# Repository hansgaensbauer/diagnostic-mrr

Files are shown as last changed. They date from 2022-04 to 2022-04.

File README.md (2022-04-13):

# Low Cost MRR For Malaria Diagnosis

This project is a low-cost, low complexity version of the instrument presented by Peng, Chen, and Han in [Development of miniaturized, portable magnetic resonance relaxometry system for point-of-care medical diagnosis](https://aip.scitation.org/doi/citedby/10.1063/1.4754296), used by Peng et al. in [Micromagnetic resonance relaxometry for rapid label-free malaria diagnosis](https://www.nature.com/articles/nm.3622). 

This tool attempts to significantly lower the cost of an instrument capable of diagnosing malaria and other diseases by stripping the researchers' design of all functionality that is not absolutely necessary for this specific application. Notably, this is done by:
1. Modifying the magnet holder so that the separation between the magnets on either side of the sample can be adjusted. This allows the larmor frequency for proton MRR to be tuned to an easily obtaiable frequency. 
2. Generating the CPMG pulse train and the 20MHz carrier with a cheap microcontroller (ATMEGA328P)
3. Replacing COTS RF components with custom implementations using cheap passives and transistors wherever possible
4. Implementing the receiver with tuned filters and peak detect circuits

## New Hardware
These PCBs have been ordered, manufactured, and shipped. They will make testing and calibration much more controlled and repeatable. 
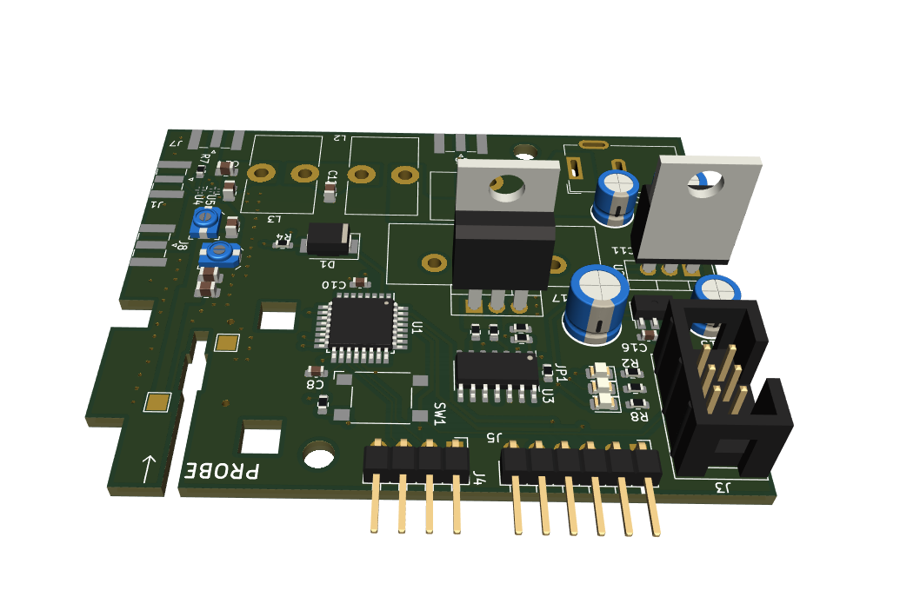
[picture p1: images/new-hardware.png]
New PCB


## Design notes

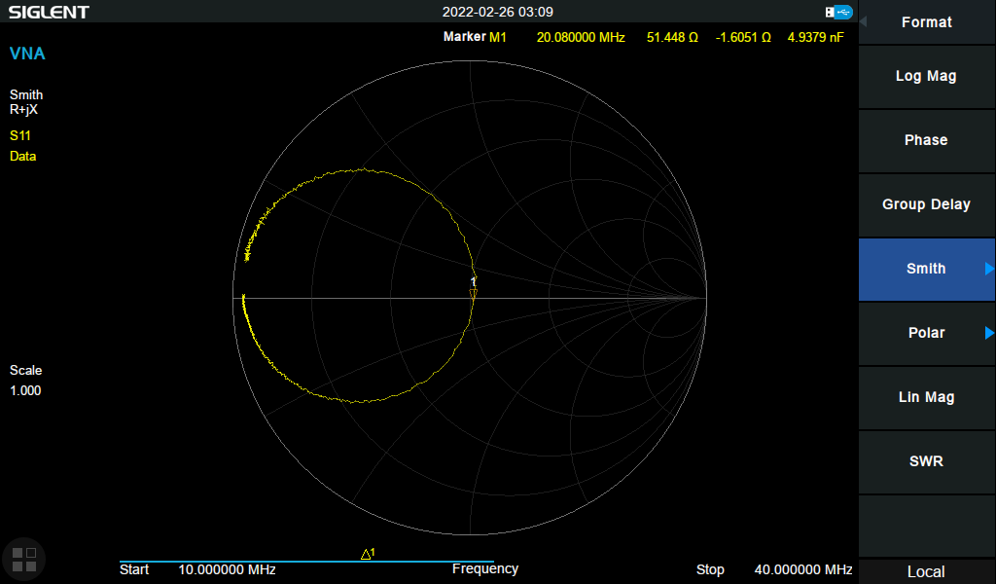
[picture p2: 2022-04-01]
images/Probe-Smith.png

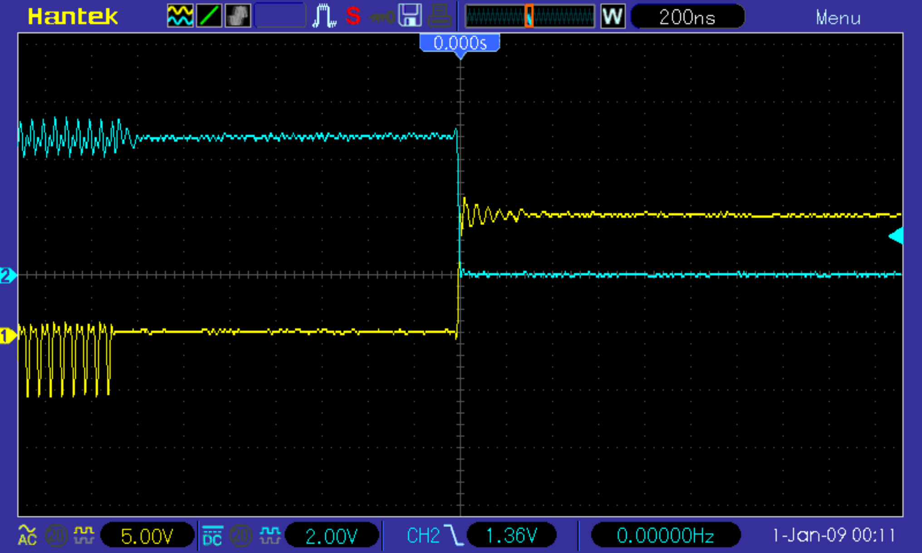
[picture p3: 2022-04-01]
images/dead-time.png

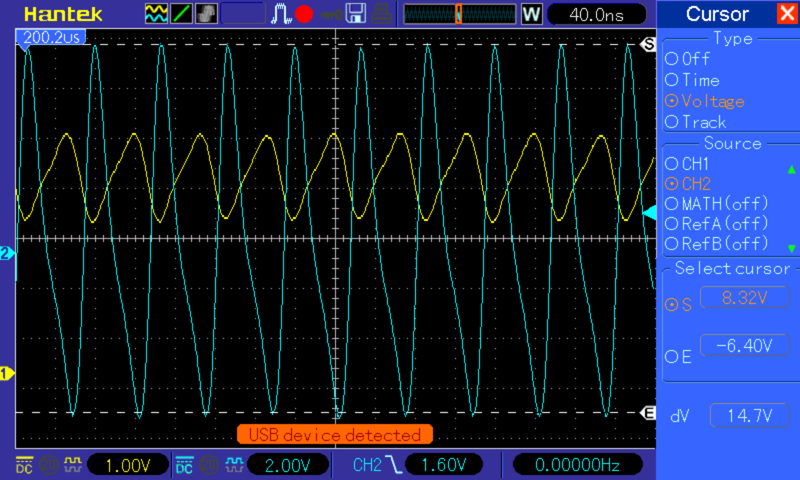
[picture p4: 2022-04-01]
images/pa-1w.png

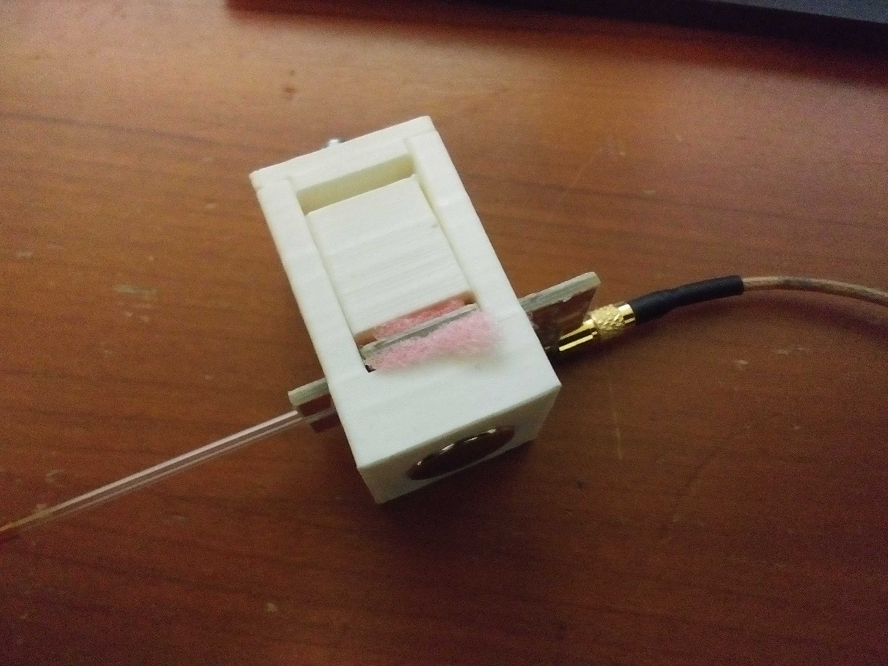
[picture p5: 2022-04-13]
images/Probe-V1.jpg

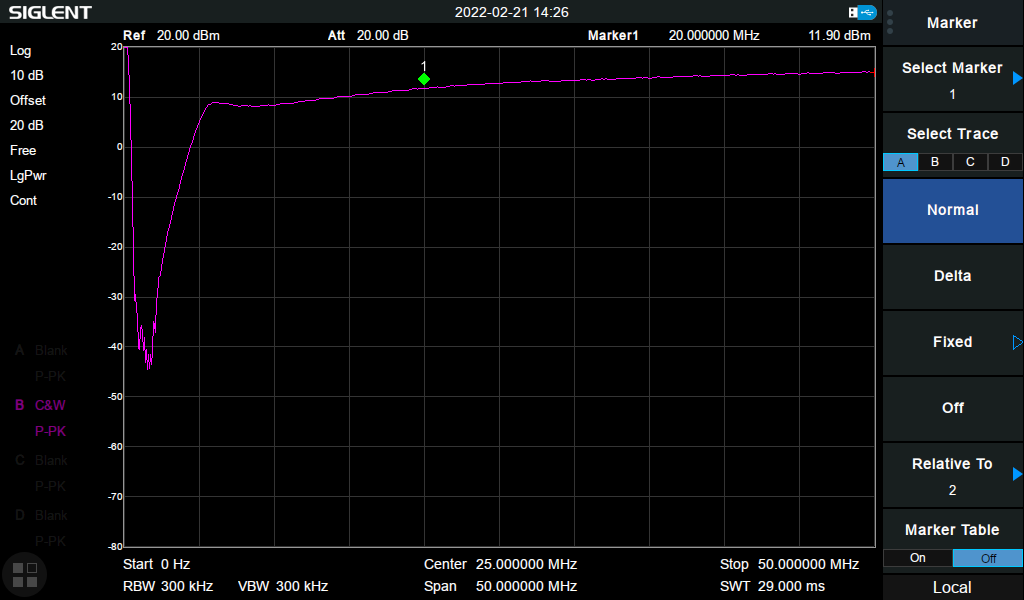
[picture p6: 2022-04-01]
images/rtl-sdr-lna.png

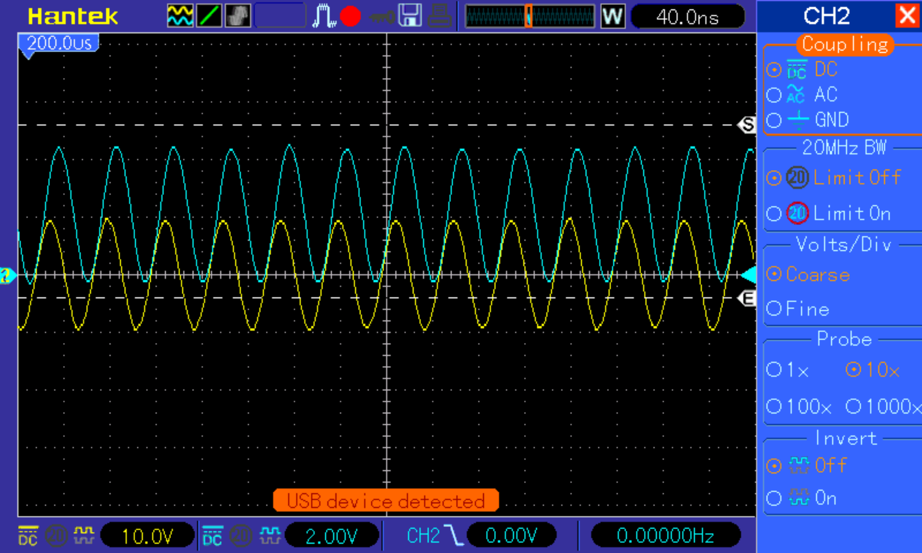
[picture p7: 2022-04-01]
images/pa-firstpass.png

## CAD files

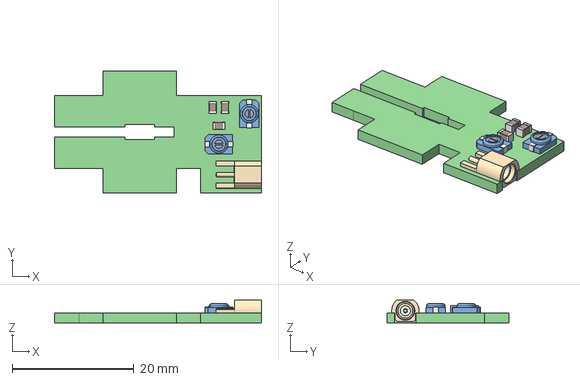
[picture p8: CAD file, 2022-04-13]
Hardware/probe/probe.step
34.0 x 20.0 x 3.75 mm
probe PCB

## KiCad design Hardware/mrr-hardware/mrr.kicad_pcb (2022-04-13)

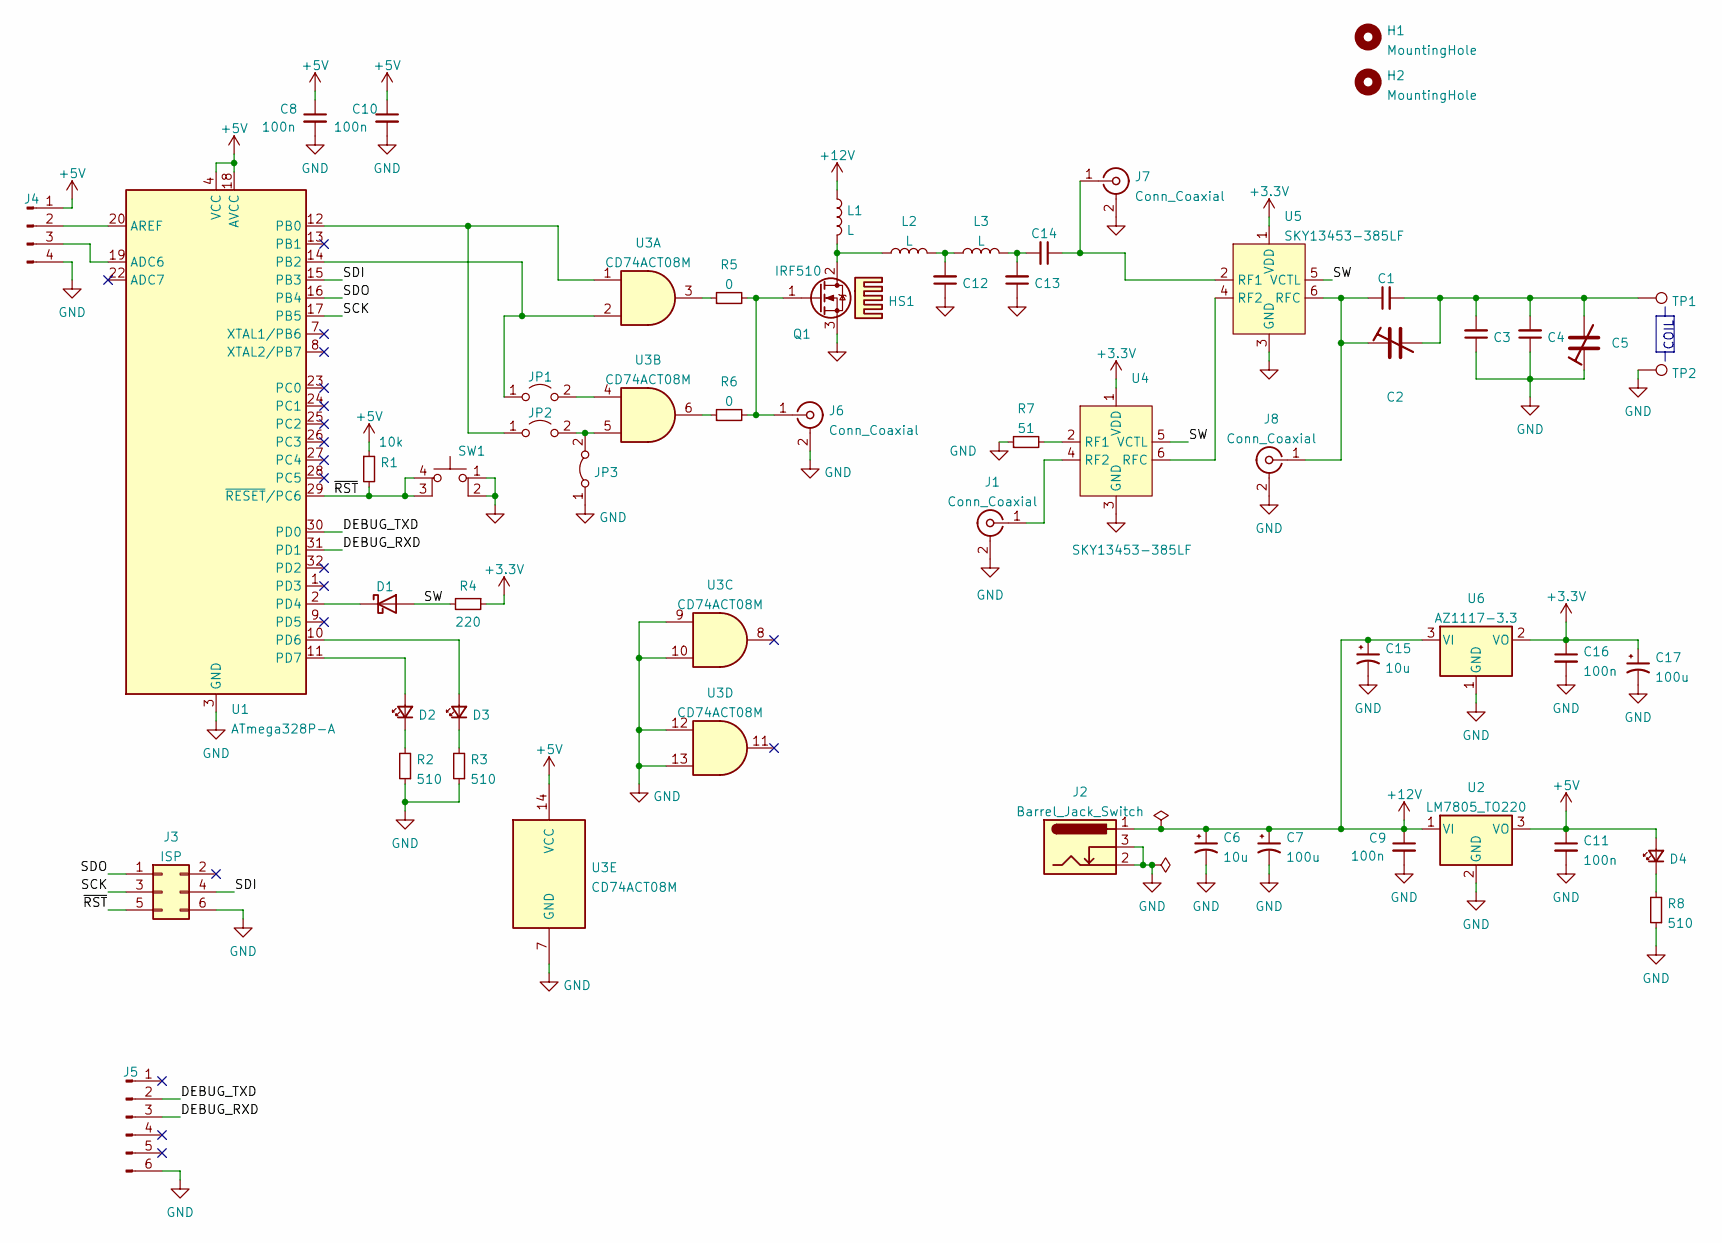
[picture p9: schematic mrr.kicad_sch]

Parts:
C1, C3, C4, C12, C13, C14: C_Small; C_0805_2012Metric
C2, C5: C_Trim; C_Trimmer_Sprague-Goodman_SGC3
C6, C15: 10u; CP_Radial_D5.0mm_P2.00mm
C7, C17: 100u; CP_Radial_D6.3mm_P2.50mm
C8, C9, C10, C11, C16: 100n; C_0603_1608Metric
D1: D_Schottky; D_SMB
D2, D3, D4: LED_Small; LED_0805_2012Metric
H1, H2: MountingHole; MountingHole_3.2mm_M3
HS1: Heatsink; BIG_HEATSINK
J1, J6, J7, J8: Conn_Coaxial; SMA_Samtec_SMA-J-P-X-ST-EM1_EdgeMount
J2: Barrel_Jack_Switch; BarrelJack_Wuerth_6941xx301002
J3: ISP; IDC-Header_2x03_P2.54mm_Vertical
J4: Conn_01x04_Male; PinHeader_1x04_P2.54mm_Horizontal
J5: Conn_01x06_Male; PinHeader_1x06_P2.54mm_Horizontal
JP1, JP2: Jumper_2_Open; R_0603_1608Metric
JP3: Jumper_2_Bridged; R_0603_1608Metric
L1, L2, L3: L; L_Toroid_Vertical_L14.7mm_W8.6mm_P5.58mm_Pulse_KM-1
Q1: IRF510; TO-220-3_Vertical
R1: 10k; R_0603_1608Metric
R2, R3, R8: 510; R_0603_1608Metric
R4: 220; R_0603_1608Metric
R5, R6: 0; R_0603_1608Metric
R7: 51; R_0603_1608Metric
SW1: SW_MEC_5E; SW_SPST_Omron_B3FS-100xP
TP1, TP2: TestPoint; TestPoint_Pad_2.0x2.0mm
U1: ATmega328P-A; TQFP-32_7x7mm_P0.8mm
U2: LM7805_TO220; TO-220-3_Vertical
U3: CD74ACT08M; SOIC-14_3.9x8.7mm_P1.27mm
U4, U5: SKY13453-385LF; 6-XFQFN
U6: AZ1117-3.3; SOT-89-3

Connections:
+3V3: C16.1, C17.1, R4.1, U4.1 (VDD), U5.1 (VDD), U6.2 (VO)
+5V: C8.1, C10.1, C11.1, D4.2 (A), J4.1, R1.1, U1.4 (VCC), U1.6 (VCC), U1.18 (AVCC), U2.3 (VO), U3.14 (VCC)
+12V: C6.1, C7.1, C9.1, C15.1, J2.1, L1.1, U2.1 (VI), U6.3 (VI)
/DEBUG_RXD: J5.3, U1.31 (PD1)
/DEBUG_TXD: J5.2, U1.30 (PD0)
/SCK: J3.3, U1.17 (PB5)
/SDI: J3.4, U1.15 (PB3)
/SDO: J3.1, U1.16 (PB4)
/SW: D1.2 (A), R4.2, U4.5 (VCTL), U5.5 (VCTL)
/~RST: J3.5, R1.2, SW1.3 (K), SW1.4 (A), U1.29 (~RESET/PC6)
GND: C3.1, C4.1, C5.1, C6.2, C7.2, C8.2, C9.2, C10.2, C11.2, C12.1, C13.1, C15.2, C16.2, C17.2, J1.2 (Ext), J2.2, J2.3, J3.6, J4.4, J5.6, J6.2 (Ext), J7.2 (Ext), J8.2 (Ext), JP3.1 (A), Q1.3 (S), R2.1, R3.1, R7.1, R8.1, SW1.1, SW1.2, TP2.1, U1.3 (GND), U1.5 (GND), U1.21 (GND), U2.2 (GND), U3.7 (GND), U3.9, U3.10, U3.12, U3.13, U4.3 (GND), U5.3 (GND), U6.1 (GND)
unnamed: C1.1, C2.1, J8.1 (In), U5.6 (RFC)
unnamed: C1.2, C2.2, C3.2, C4.2, C5.2, TP1.1
unnamed: C12.2, L2.2, L3.1
unnamed: C13.2, C14.2, L3.2
unnamed: C14.1, J7.1 (In), U5.2 (RF1)
unnamed: D1.1 (K), U1.2 (PD4)
unnamed: D2.1 (K), R2.2
unnamed: D2.2 (A), U1.11 (PD7)
unnamed: D3.1 (K), R3.2
unnamed: D3.2 (A), U1.10 (PD6)
unnamed: D4.1 (K), R8.2
unnamed: J1.1 (In), U4.4 (RF2)
unnamed: J4.2, U1.20 (AREF)
unnamed: J4.3, U1.19 (ADC6)
unnamed: J6.1 (In), Q1.1 (G), R5.2, R6.2
unnamed: JP1.1 (A), U1.14 (PB2), U3.2
unnamed: JP1.2 (B), U3.4
unnamed: JP2.1 (A), U1.12 (PB0), U3.1
unnamed: JP2.2 (B), JP3.2 (B), U3.5
unnamed: L1.2, L2.1, Q1.2 (D)
unnamed: R5.1, U3.3
unnamed: R6.1, U3.6
unnamed: R7.2, U4.2 (RF1)
unnamed: U4.6 (RFC), U5.4 (RF2)

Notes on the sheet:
COIL

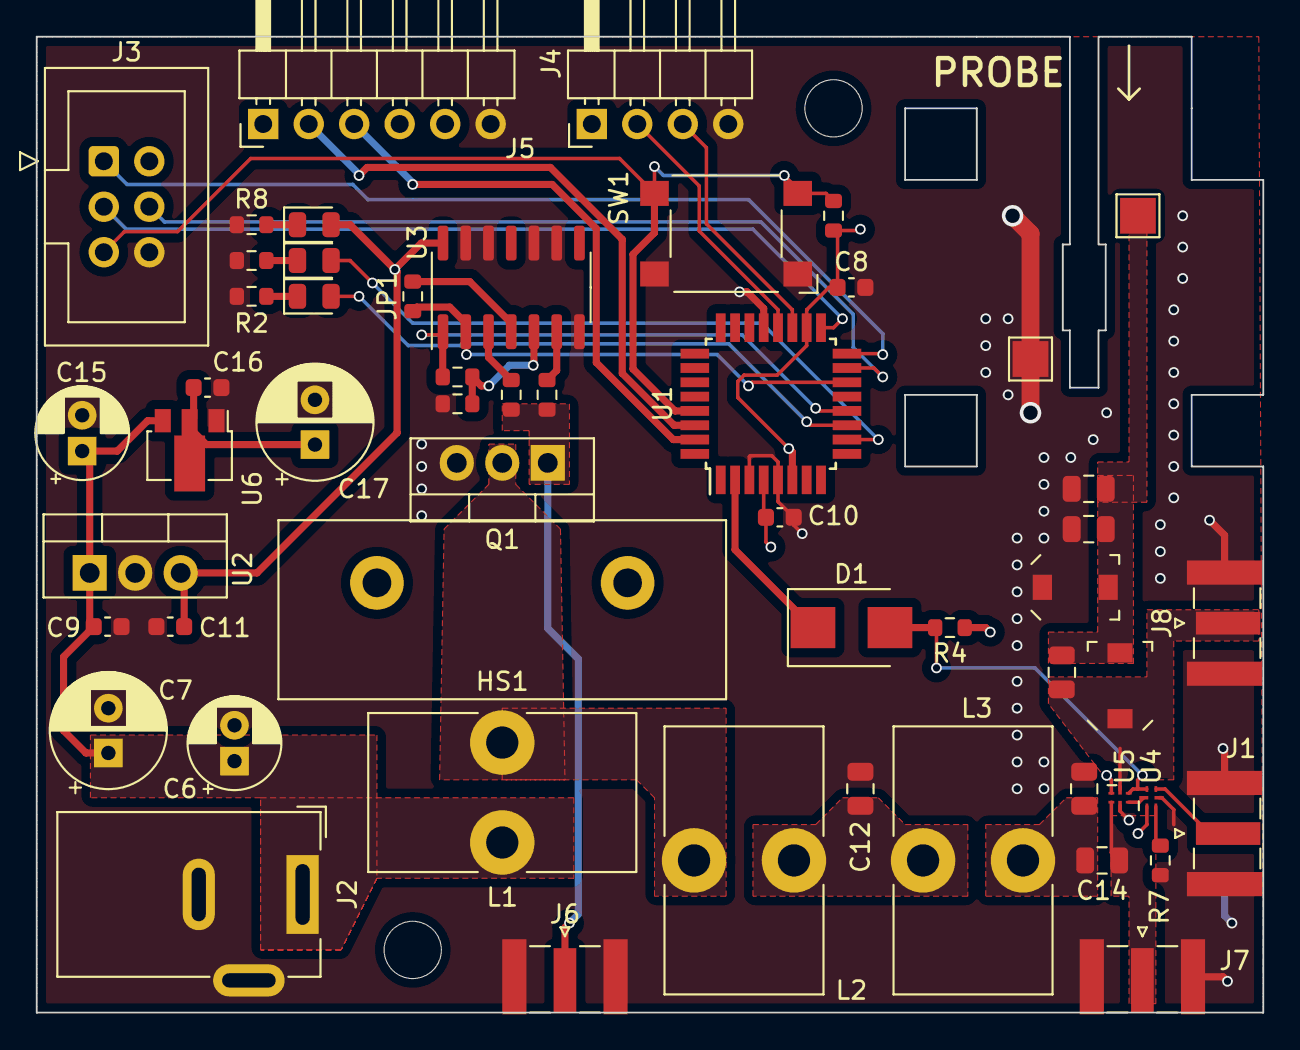
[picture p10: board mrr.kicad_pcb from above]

Board: 4 copper layers, 68.5 x 54.5 mm, 56 parts (0 on the bottom side), 35 nets.

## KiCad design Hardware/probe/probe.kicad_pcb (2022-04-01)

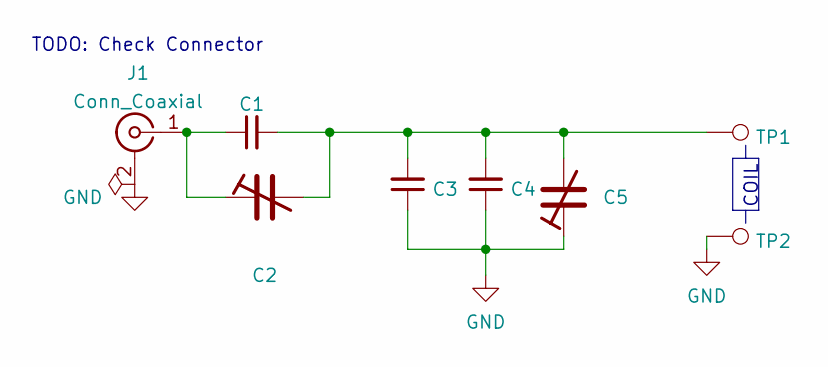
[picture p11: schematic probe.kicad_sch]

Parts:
C1, C3, C4: C_Small; C_0805_2012Metric
C2, C5: C_Trim; C_Trimmer_Sprague-Goodman_SGC3
J1: Conn_Coaxial; MMCX_Molex_73415-0961_Horizontal_1.0mm-PCB
TP1, TP2: TestPoint; TestPoint_Pad_2.0x2.0mm

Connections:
GND: C3.1, C4.1, C5.1, J1.2 (Ext), TP2.1
unnamed: C1.1, C2.1, J1.1 (In)
unnamed: C1.2, C2.2, C3.2, C4.2, C5.2, TP1.1

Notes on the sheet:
TODO: Check Connector
COIL

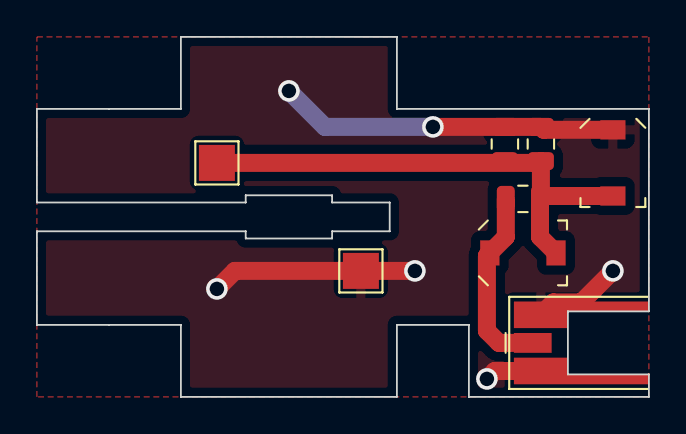
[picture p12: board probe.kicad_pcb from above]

Board: 2 copper layers, 34.0 x 20.0 mm, 8 parts (0 on the bottom side), 3 nets.

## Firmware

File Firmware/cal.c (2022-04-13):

/* Program for determining the 90 and 180 degree pulse lengths
*
* Sweeps through a sequence of 90-180-wait, with a trigger signal
* after the 180 degree wait signal.  
*
* This code uses the fast PWM mode of operation of the 
* 16 bit timer/counter 1 to generate the required pulse
* widths at the desired pulse repetition rate.
*
* This code should be run with FCLK = 20MHz, and CLKO enabled.
* PD4 - RF Switch Control
* PD0 - Trigger Output
* PB2 - Modulation Control
* PB0 - 20MHz Out
*/

#include <avr/io.h>
#include <avr/interrupt.h>
#include <util/delay.h>
#include "mrr.h"

//Pulsewidths to try, in μs
#define NUM_PW 10
uint8_t pulsewidths[NUM_PW] = {10, 20, 30, 40, 50, 60, 70, 80, 90, 100};

//This flag is set after the 180 degree pulse is set up so that the trigger signal
//doesn't fire during the 90 degree pulse
volatile uint8_t echo_ready_flag = 0;

//This flag is used to set up the trigger signal after we enter the echo period
volatile uint8_t trig_ready_flag = 0;

int main(void) {

    //Connect coil to transmiter
    DDRD |= 0b00010001;
    PORTD = 0b00010000;

    TCCR1A = 0b00100011; //Fast PWM, TOP=OCR1A, non inverting for OC1B
    TCCR1B = 0b00011000; //Fast PWM, TOP=OCR1A, CS12:0 = CLK_IO/1.
    DDRB |= 0b00000100; //Set PB2/OC1B to output

    TIMSK1 |= 0b00000110; //Enable Compare A + B Match Interrupts
    sei(); //Enable global interrupts

    //Set up the inter-pulse spacing
    OCR1A = ((PULSETRAIN_DELAY) * (F_CPU / 1000000UL)); //20 cycles/μs * PULSE_SPACINGμs
    

    for(uint8_t i = 0; i < NUM_PW; i++){
        
        trig_ready_flag = 0;
        echo_ready_flag = 0;

	TCCR1A = 0b00100011; 

	//Set up the 90 degree pulse
	echo_ready_flag = 0;
	uint8_t pw_90 = pulsewidths[i];
        OCR1B = ((pw_90) * (F_CPU / 1000000UL)); //90 degree pulse, 20 cycles/μs * 2 * pw_90μs
    
	TCCR1B = 0b00011001; //Fast PWM, TOP=OCR1A, CS12:0 = CLK_IO/1. Turn on timer
    
	//Immediately switch to pulse spacing and 180 degree pulsewidth
        OCR1B = ((pw_90 * 2) * (F_CPU / 1000000UL)); //180 degree pulse, 20 cycles/μs * 2 * pw_90μs

	_delay_ms(1000); //wait one second between repeated trials

	PORTD &= ~0b00000001; //clear the trigger signal
    }

    cli(); //turn off all interrupts

    while (1); //do nothing

}

//Timer 1 Compare B Match Interrupt
//Execute Every time we switch off the RF pulse
ISR(TIMER1_COMPB_vect) {
    PORTD = 0;
    if(echo_ready_flag){
	PORTB &= ~0b00000100; //make sure PB2 stays low
	TCCR1A = 0b00000011; //disconnect OC1B
	trig_ready_flag = 1;
	echo_ready_flag = 0;
    } else {
        echo_ready_flag = 1;
    }
}

//Timer 1 Compare A Match Interrupt
//Execute Every time we switch on the RF coil
ISR(TIMER1_COMPA_vect) {
    if(trig_ready_flag){
	PORTD |= 0b00000001;
        TCCR1B = 0b00011000; //Turn off the timer
	TCNT1 = 0; //Clear the timer
	trig_ready_flag = 0;
    } else{
        PORTD |= 0b00010000;
    }
}

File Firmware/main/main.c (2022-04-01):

/* Main source for low cost malaria diagnosis NMR 
*
* This code uses the fast PWM mode of operation of the 
* 16 bit timer/counter 1 to generate the required pulse
* widths at the desired pulse repetition rate.
*
* This code should be run with FCLK = 20MHz, and CLKO enabled.
* PD4 - RF Switch Control
* PB2 - Modulation Control
* PB0 - 20MHz Out
*/

#include <avr/io.h>
#include <avr/interrupt.h>
#include "nmr.h"

volatile int pulse_count; //count up to numpulses

int main(void) {

    //Connect coil to transmiter
    DDRD |= 0b00011000;
    PORTD = 0b00010000;

    pulse_count = 0; //reset pulse count

    TCCR1A = 0b00100011; //Fast PWM, TOP=OCR1A, non inverting for OC1B
    TCCR1B = 0b00011000; //Fast PWM, TOP=OCR1A, CS12:0 = CLK_IO/1.
    DDRB |= 0b00000110; //Set PB2/OC1B to output

    TIMSK1 |= 0b00000110; //Enable Compare A + B Match Interrupts
    sei(); //Enable global interrupts

    OCR1B = ((PULSEWIDTH_90) * (F_CPU / 1000000UL)); //90 degree pulse, 20 cycles/μs * 2 * PULSEWIDTH_90μs
    OCR1A = ((PULSETRAIN_DELAY) * (F_CPU / 1000000UL)); //20 cycles/μs * PULSE_SPACINGμs

    TCCR1B = 0b00011001; //Fast PWM, TOP=OCR1A, CS12:0 = CLK_IO/1. Turn on timer

    //Immediately switch to pulse spacing and 180 degree pulsewidth
    OCR1B = ((PULSEWIDTH_90 * 2) * (F_CPU / 1000000UL)); //180 degree pulse, 20 cycles/μs * 2 * PULSEWIDTH_90μs
    OCR1A = ((PULSE_SPACING) * (F_CPU / 1000000UL)); //20 cycles/μs * PULSE_SPACINGμs

    while (pulse_count < NUMPULSES); //Wait for the required number of pulses

    cli(); //turn off all interrupts
    TCCR1B = 0b00011000; //Turn off the timer

    while (1); //do nothing

}

//Timer 1 Compare B Match Interrupt
//Execute Every time we switch off the RF pulse
ISR(TIMER1_COMPB_vect) {
    pulse_count ++;
    PORTD = 0;
}

//Timer 1 Compare A Match Interrupt
//Execute Every time we switch on the RF coil
ISR(TIMER1_COMPA_vect) {
    PORTD = 0b00011000;
}

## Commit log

2022-04-01 Initial Commit
    Add existing project files to repo.
    [probe-B_Cu.gbr, probe-Edge_Cuts.gbr, probe-F_Cu.gbr, probe-job.gbrjob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]
2022-04-13 Update Makefile
    Reorganized project to make flashing calibration firmware cleaner
2022-04-13 Re-add hardware
    [mrr.kicad_pcb, mrr.kicad_sch, probe-B_Cu.gbr, probe-Edge_Cuts.gbr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]
2022-04-13 Add stashed changes
    [probe.step]
2022-04-13 Add new hardware images
    [mrr.kicad_pcb]
